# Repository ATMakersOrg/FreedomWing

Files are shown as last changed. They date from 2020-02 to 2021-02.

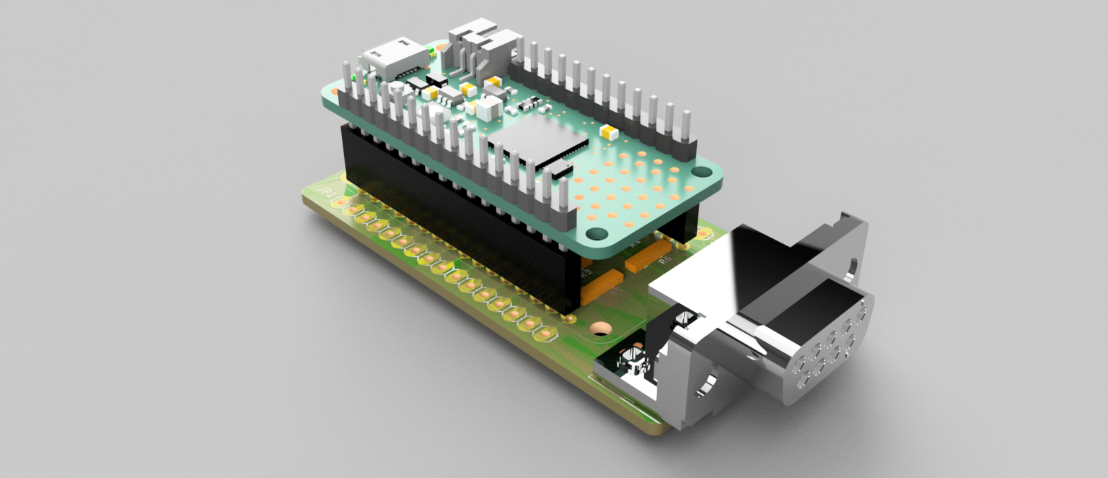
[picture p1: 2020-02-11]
hardware/case/FreedomWing v21.png

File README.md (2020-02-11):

# FreedomWing
Code and Hardware necessary to make the FreedomWing Joystick Adapter

Software is licensed under the MIT Open Source license.  A copy is provided in the 'software' subdirectory
Hardware designs are licensed under the Creative Commons Attribution Share Alike (CC-BY:SA) license.  A copy is provided in the 'hardware' subdirectory.

Documentation is in development and will be hosted at http://atmakers.org/featherwing

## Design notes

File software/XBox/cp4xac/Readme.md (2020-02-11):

Because of limitations in the XBox Adaptive Controller's USB implementation, the FreedomWing will need a special version of CircuitPython that limits the HID profiles.
If you are using a Feather M4, you can use the .UF2 file in this directory - it is known to work.

Otherwise, please find the appropriate .UF2 file in the cp4xac repository on GitHub here:
https://github.com/ATMakersBill/cp4xac

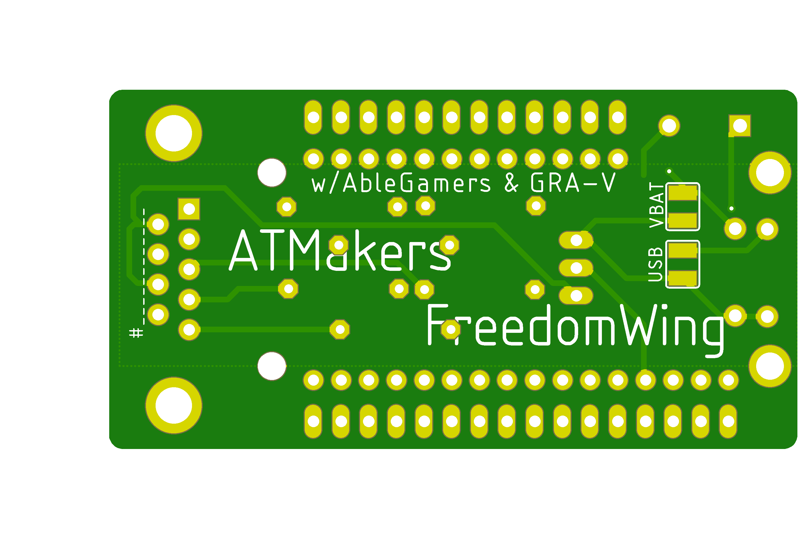
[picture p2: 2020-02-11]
hardware/pcb/FreedomWingBot.png

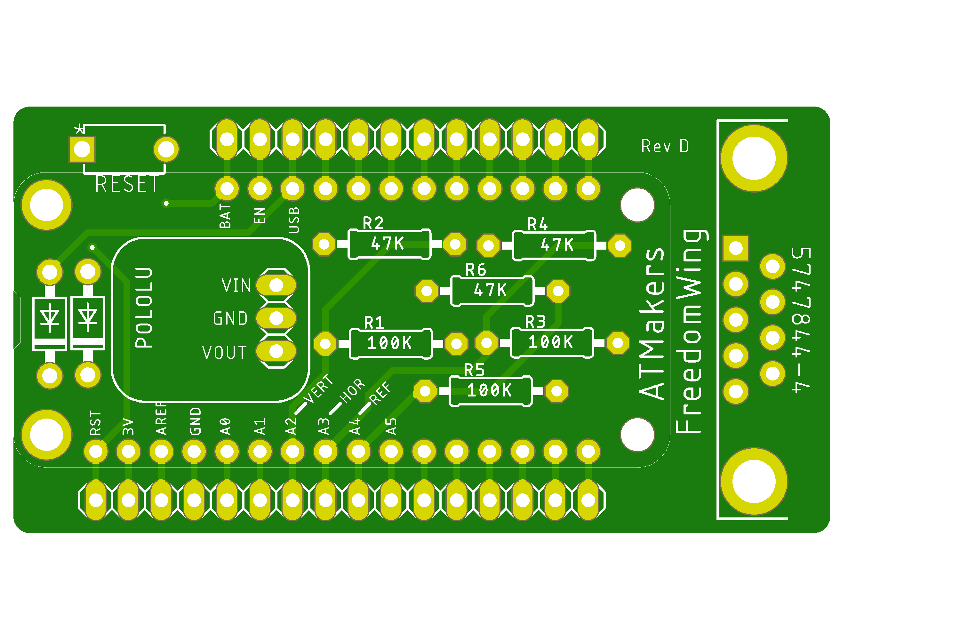
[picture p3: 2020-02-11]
hardware/pcb/FreedomWingTop.png

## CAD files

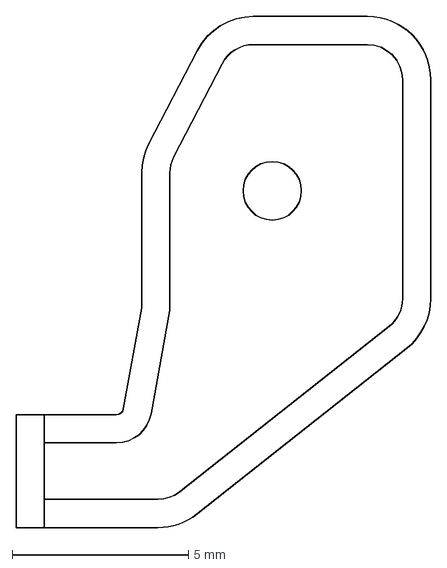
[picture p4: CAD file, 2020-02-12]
hardware/case/ResetTab.dxf
11.8 x 14.5 mm

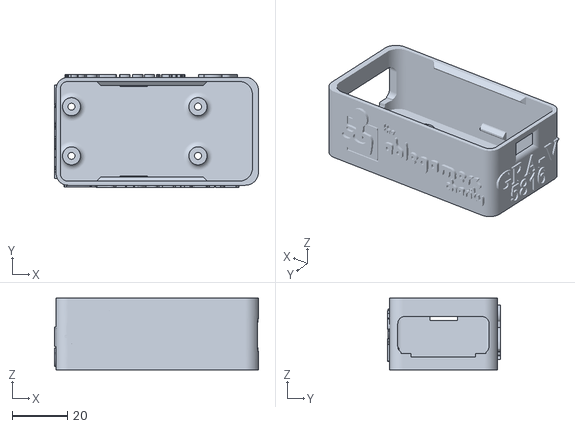
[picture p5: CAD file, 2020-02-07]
hardware/case/FreedomWingCase.stl
73.7 x 40.8 x 26.0

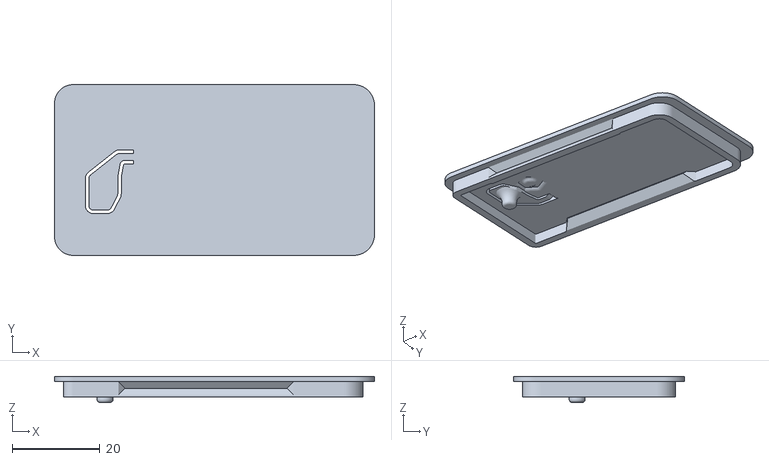
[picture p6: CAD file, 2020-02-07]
hardware/case/FreedomWingLid.stl
73.1 x 39.0 x 5.94

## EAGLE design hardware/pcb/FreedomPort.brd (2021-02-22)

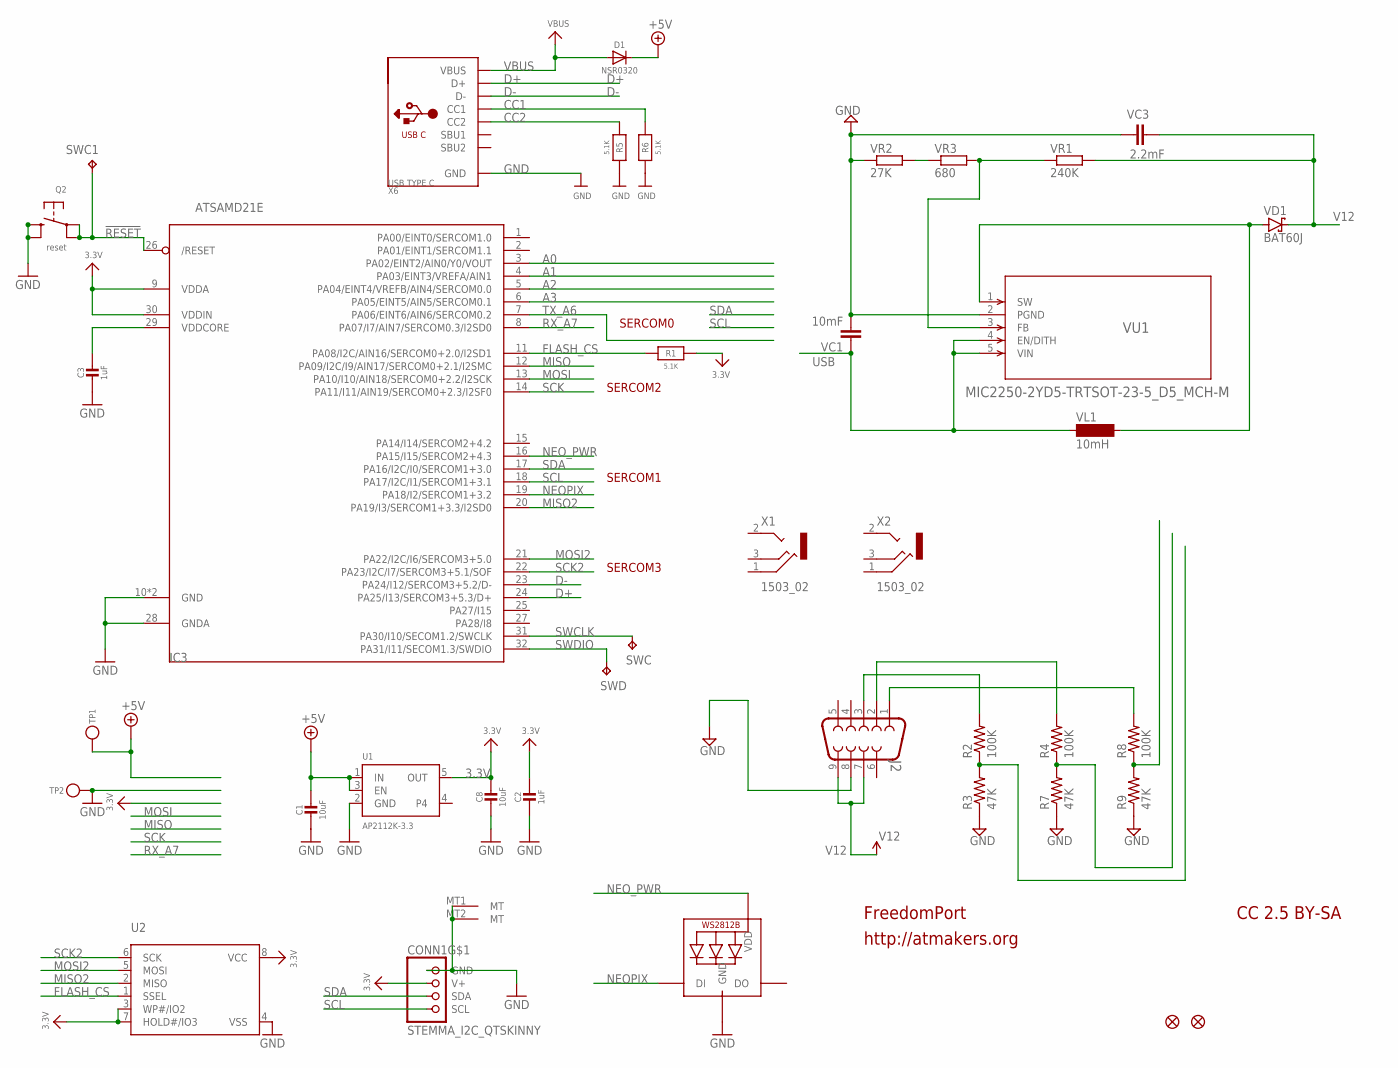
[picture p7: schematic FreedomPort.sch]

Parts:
C1, C8: 10uF; _0805MP
C2, C3: 1uF; _0402NO
CONN1: STEMMA_I2C_QTSKINNY; JST_SH4_SKINNY
D1: NSR0320; SOD-323_MINI
IC3: ATSAMD21E; QFN32_5MM
J2: DB9MALE; DB9_MALE
LED1: WS2812B_SK6805_1515; SK6805_1515
Q2: reset; BTN_KMR2_4.6X2.8
R1, R5, R6: 5.1K; _0402NO
R2, R4, R8: 100K; R0805
R3, R7, R9: 47K; R0805
SWC, SWC1: TPB1,27; B1,27
SWD: TPB1,27; B1,27
TP1, TP2: TESTPOINT_1X3; TESTPOINT_RECT_1X3MM
U1: AP2112K-3.3; SOT23-5
U2: SPIFLASH_8PIN; SOIC8_150MIL
U$6, U$8: FIDUCIAL_1MM
VC1: 10mF; C0805
VC3: 2.2mF; C0805
VD1: BAT60J; SOD323_ST
VL1: 10mH; MS50
VR1: 240K; R0805W
VR2: 27K; R0805W
VR3: 680; R0805W
VU1: MIC2250-2YD5-TRTSOT-23-5_D5_MCH-M; TSOT-23-5_D5_MCH-M
X1, X2: 1503_02
X6: USB TYPE C; USB_C_CUSB31-CFM2AX-01-X

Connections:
3.3V: C2.1, C8.1, CONN1.2 (V+), IC3.9 (VDDA), IC3.30 (VDDIN), R1.1, U1.5 (OUT), U2.3 (WP#/IO2), U2.7 (HOLD#/IO3), U2.8 (VCC)
!RESET: IC3.26 (/RESET), Q2.A, Q2.A' (P1), SWC1.TP
+5V: C1.1, D1.C, TP1.P$1, U1.1 (IN), U1.3 (EN)
A0: IC3.3 (PA02/EINT2/AIN0/Y0/VOUT)
A1: IC3.4 (PA03/EINT3/VREFA/AIN1)
A2: IC3.5 (PA04/EINT4/VREFB/AIN4/SERCOM0.0)
A3: IC3.6 (PA05/EINT5/AIN5/SERCOM0.1)
CC1: R6.2, X6.A5 (CC1)
CC2: R5.2, X6.B5 (CC2)
D+: IC3.24 (PA25/I13/SERCOM3+5.3/D+), X6.A6 (D+), X6.B6 (D+)
D-: IC3.23 (PA24/I12/SERCOM3+5.2/D-), X6.A7 (D-), X6.B7 (D-)
FLASH_CS: IC3.11 (PA08/I2C/AIN16/SERCOM0+2.0/I2SD1), R1.2, U2.1 (SSEL)
GND: C1.2, C2.2, C3.2, C8.2, CONN1.1 (GND), CONN1.MT1 (MT), CONN1.MT2 (MT), IC3.10 (GND), IC3.28 (GNDA), IC3.33 (GND), J2.8, LED1.4 (GND), Q2.B (S), Q2.B' (S1), R3.1, R5.1, R6.1, R7.1, R9.1, TP2.P$1, U1.2 (GND), U2.4 (VSS), VC1.2, VC3.1, VR2.1, VU1.2 (PGND), X6.A1B12 (GND), X6.B1A12 (GND)
MISO: IC3.12 (PA09/I2C/I9/AIN17/SERCOM0+2.1/I2SMC)
MISO2: IC3.20 (PA19/I3/SERCOM1+3.3/I2SD0), U2.2 (MISO)
MOSI: IC3.13 (PA10/I10/AIN18/SERCOM0+2.2/I2SCK)
MOSI2: IC3.21 (PA22/I2C/I6/SERCOM3+5.0), U2.5 (MOSI)
unnamed: J2.3, R2.2
unnamed: R2.1, R3.2
unnamed: R4.1, R7.2
unnamed: R8.1, R9.2
unnamed: VR1.1, VR3.2, VU1.3 (FB)
unnamed: J2.2, R4.2
unnamed: J2.1, R8.2
unnamed: VD1.A, VL1.2, VU1.1 (SW)
unnamed: VR2.2, VR3.1
NEOPIX: IC3.19 (PA18/I2/SERCOM1+3.2), LED1.1 (DI)
NEO_PWR: IC3.16 (PA15/I15/SERCOM2+4.3), LED1.2 (VDD)
RX_A7: IC3.8 (PA07/I7/AIN7/SERCOM0.3/I2SD0)
SCK: IC3.14 (PA11/I11/AIN19/SERCOM0+2.3/I2SF0)
SCK2: IC3.22 (PA23/I2C/I7/SERCOM3+5.1/SOF), U2.6 (SCK)
SCL: CONN1.4 (SCL), IC3.18 (PA17/I2C/I1/SERCOM1+3.1)
SDA: CONN1.3 (SDA), IC3.17 (PA16/I2C/I0/SERCOM1+3.0)
SWCLK: IC3.31 (PA30/I10/SECOM1.2/SWCLK), SWC.TP
SWDIO: IC3.32 (PA31/I11/SECOM1.3/SWDIO), SWD.TP
TX_A6: IC3.7 (PA06/EINT6/AIN6/SERCOM0.2)
USB: VC1.1, VL1.1, VU1.4 (EN/DITH), VU1.5 (VIN)
V12: J2.7, J2.9, VC3.2, VD1.C, VR1.2
VBUS: D1.A, X6.A4B9 (VBUS), X6.B4A9 (VBUS)
VDDCORE: C3.1, IC3.29 (VDDCORE)

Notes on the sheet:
FreedomPort
http://atmakers.org
CC 2.5 BY-SA
SERCOM0
SERCOM1
SERCOM2
SERCOM3

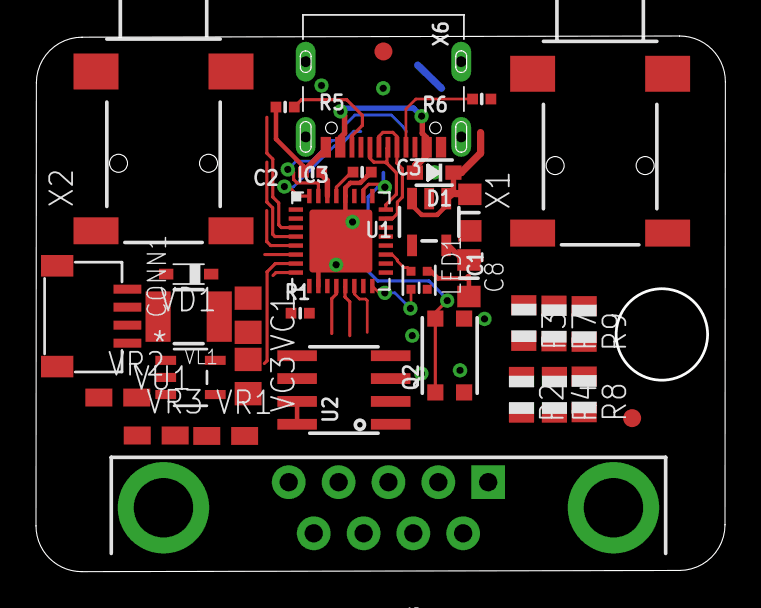
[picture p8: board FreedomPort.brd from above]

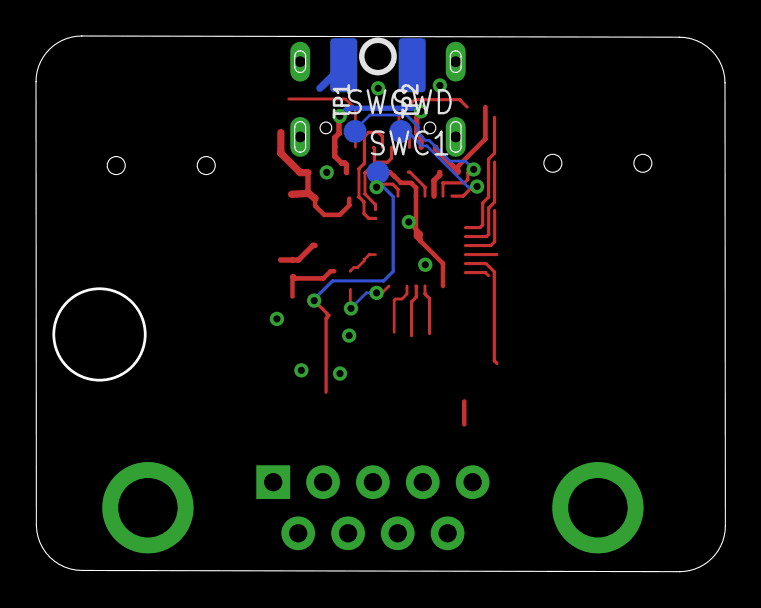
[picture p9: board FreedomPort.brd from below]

Board: 2 copper layers, 38.3 x 29.8 mm, 42 parts (7 on the bottom side), 31 nets.

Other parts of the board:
U$11: QTPY_BOT
U$12: PCBFEAT-REV-040
U$13: QTPY_TOP

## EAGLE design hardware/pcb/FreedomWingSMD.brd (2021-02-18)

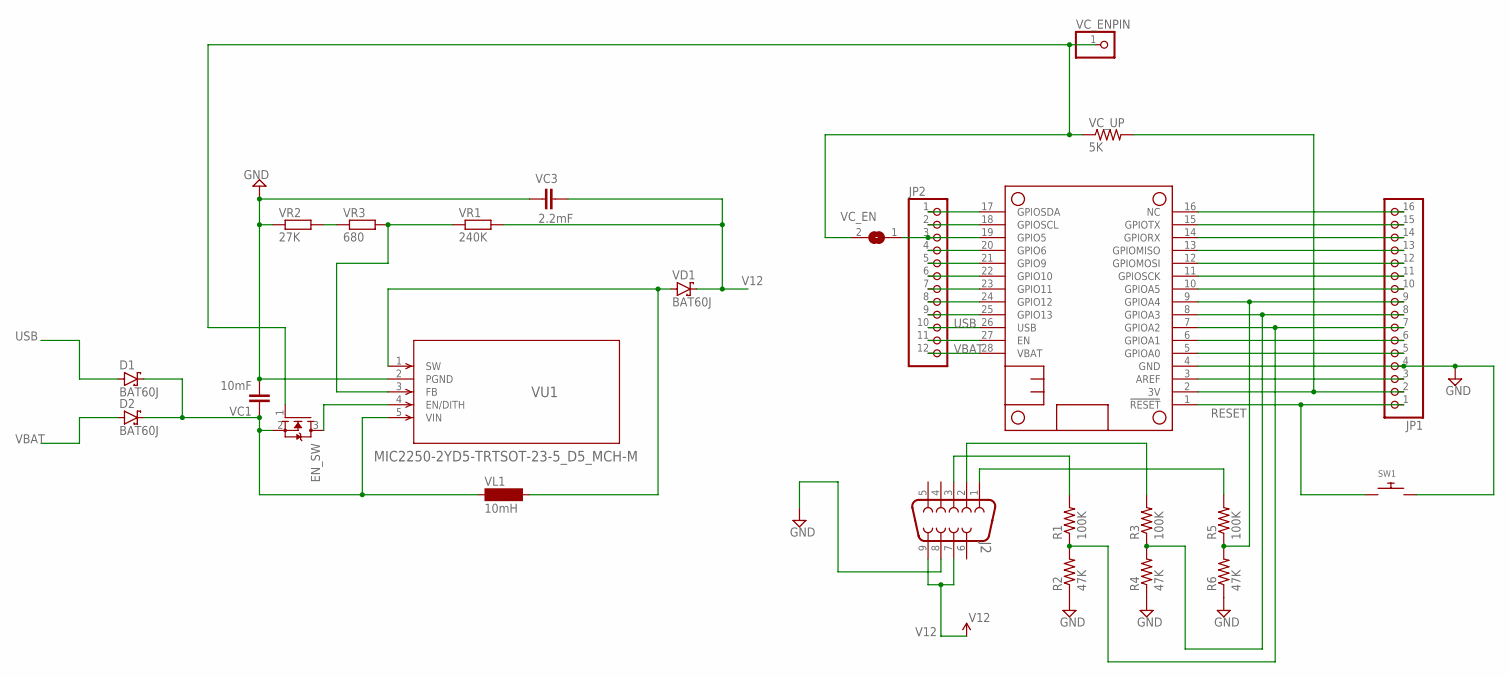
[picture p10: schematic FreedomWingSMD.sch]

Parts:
D1, D2: BAT60J; SOD323_ST
EN_SW: MOSFET-NREFLOW; SOT23
J2: DB9MALE; DB9_MALE
JP1: PINHD-1X16; 1X16
JP2: PINHD-1X12; 1X12
MS1: FEATHERWING_NODIM; FEATHERWING_DIM
R1, R3, R5: 100K; R0805
R2, R4, R6: 47K; R0805
SW1: SWITCH_PUSHBUTTONC&K_KSS; BTN_CK_KSS
VC1: 10mF; C0805
VC3: 2.2mF; C0805
VC_EN: SJW
VC_ENPIN: PINHD-1X1; 1X01
VC_UP: 5K; R0805
VD1: BAT60J; SOD323_ST
VL1: 10mH; MS50
VR1: 240K; R0805W
VR2: 27K; R0805W
VR3: 680; R0805W
VU1: MIC2250-2YD5-TRTSOT-23-5_D5_MCH-M; TSOT-23-5_D5_MCH-M

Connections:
3V: JP1.2, MS1.2 (3V), VC_UP.2
GND: J2.8, JP1.4, MS1.4 (GND), R2.1, R4.1, R6.1, SW1.P$2, VC1.2, VC3.1, VR2.1, VU1.2 (PGND)
unnamed: J2.3, R1.2
unnamed: JP2.1, MS1.17 (GPIOSDA)
unnamed: JP2.2, MS1.18 (GPIOSCL)
unnamed: JP2.3, MS1.19 (GPIO5), VC_EN.1
unnamed: JP1.7, MS1.7 (GPIOA2), R1.1, R2.2
unnamed: JP1.8, MS1.8 (GPIOA3), R3.1, R4.2
unnamed: JP1.9, MS1.9 (GPIOA4), R5.1, R6.2
unnamed: VR1.1, VR3.2, VU1.3 (FB)
unnamed: J2.2, R3.2
unnamed: J2.1, R5.2
unnamed: JP2.4, MS1.20 (GPIO6)
unnamed: JP2.5, MS1.21 (GPIO9)
unnamed: JP2.6, MS1.22 (GPIO10)
unnamed: JP2.7, MS1.23 (GPIO11)
unnamed: JP2.8, MS1.24 (GPIO12)
unnamed: JP2.9, MS1.25 (GPIO13)
unnamed: JP1.10, MS1.10 (GPIOA5)
unnamed: JP1.16, MS1.16 (NC)
unnamed: JP1.15, MS1.15 (GPIOTX)
unnamed: JP1.14, MS1.14 (GPIORX)
unnamed: JP1.13, MS1.13 (GPIOMISO)
unnamed: JP1.12, MS1.12 (GPIOMOSI)
unnamed: JP1.11, MS1.11 (GPIOSCK)
unnamed: JP2.11, MS1.27 (EN)
unnamed: EN_SW.3 (D), VU1.4 (EN/DITH)
unnamed: VD1.A, VL1.2, VU1.1 (SW)
unnamed: JP1.3, MS1.3 (AREF)
unnamed: EN_SW.1 (G), VC_EN.2, VC_ENPIN.1, VC_UP.1
unnamed: JP1.6, MS1.6 (GPIOA1)
unnamed: JP1.5, MS1.5 (GPIOA0)
unnamed: VR2.2, VR3.1
RESET: JP1.1, MS1.1 (!RESET), SW1.P$1
USB: D1.A, JP2.10, MS1.26 (USB)
V12: J2.7, J2.9, VC3.2, VD1.C, VR1.2
VBAT: D2.A, JP2.12, MS1.28 (VBAT)
VMAX: D1.C, D2.C, EN_SW.2 (S), VC1.1, VL1.1, VU1.5 (VIN)

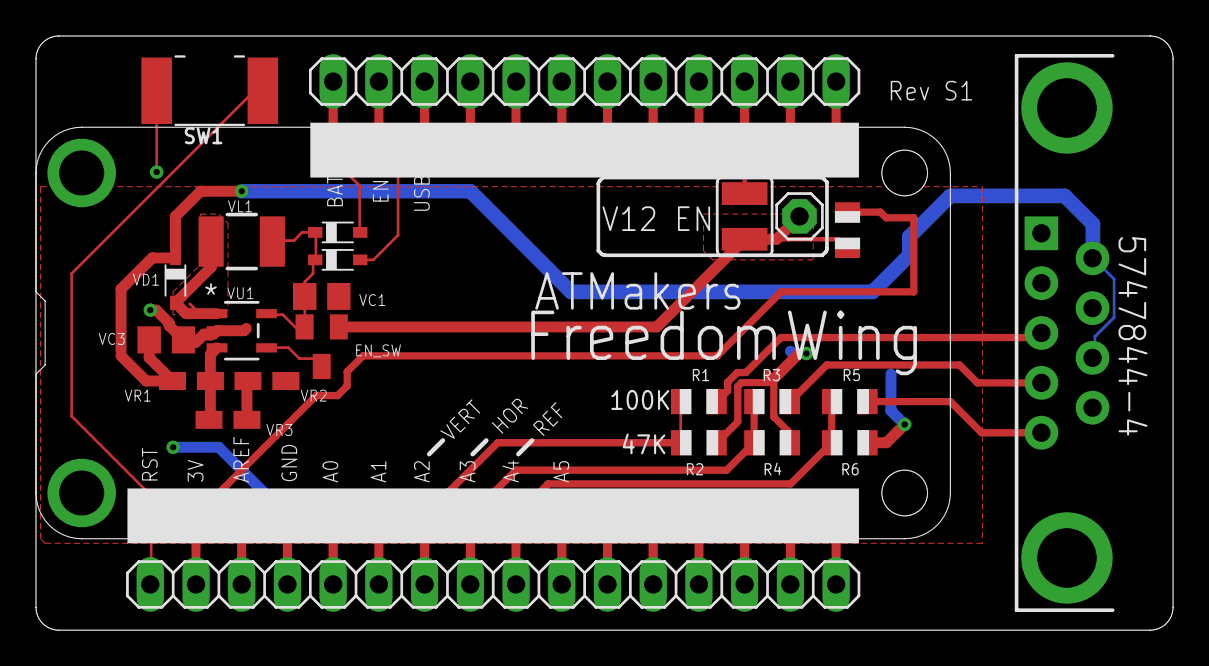
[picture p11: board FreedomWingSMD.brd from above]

Board: 2 copper layers, 63.2 x 33.0 mm, 25 parts (0 on the bottom side), 38 nets.

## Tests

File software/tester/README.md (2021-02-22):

# Tester for FreedomWing

This code (written in CircuitPython) will test a FreedomWing by using a ATMakers Virtual JoyStick board and a feather. 

Note: The Virtual Joystick PCB is in the ATMakers Hardware repository https://github.com/ATMakersOrg/ATMakers-Hardware/tree/master/JoystickWing

# Dependencies:
## CircuitPython 6+ http://circuitpython.org - choose the version for your board
## Libraries:
* neopixel
* adafruit_ds3502
* adafruit_register
* adafruit_bus_device

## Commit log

2020-02-07 Initial Release
    This is not yet baked. And I am not certain that this should all be in one repository. However, it is a starting point and I want this in version control so we have a snapshot of what was actually us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
    [FreedomWing.brd, FreedomWing.sch]
2020-02-07 Split hardware
    Also added the case files
    [FreedomWing.brd, FreedomWing.sch, FreedomWingCase.stl, FreedomWingLid.stl]
2020-02-07 First changes after Launch
    Updated to add Schottky Diodes, Reset Switch & Jumper
    [FreedomWing.brd, FreedomWing.sch]
2020-02-12 Adding Reset Tab
    [ResetTab.dxf]
2021-02-17 Adding Initial SMD Version of the FreedomWing (Untested)
    Adding Initial SMD Version of the FreedomWing (Untested)
    [FreedomWingSMD.brd, FreedomWingSMD.sch]
2021-02-18 Fixed schematic issues w/Voltage Regulator
    [FreedomWingSMD.brd, FreedomWingSMD.sch]
2021-02-18 Added values and tweaked for 12V
    [FreedomWingSMD.brd, FreedomWingSMD.sch]
2021-02-18 Switched to 2 layers & added stuff
    [FreedomWingSMD.brd, FreedomWingSMD.sch]
2021-02-22 Added a first pass at a standalone FreedomPort board
    [FreedomPort.brd, FreedomPort.sch]

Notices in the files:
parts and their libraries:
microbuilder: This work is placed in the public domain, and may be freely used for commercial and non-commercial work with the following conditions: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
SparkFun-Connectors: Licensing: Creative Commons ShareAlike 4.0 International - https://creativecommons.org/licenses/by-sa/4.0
